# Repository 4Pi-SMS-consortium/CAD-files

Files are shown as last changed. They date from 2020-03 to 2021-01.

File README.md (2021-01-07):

# CAD-files

This is a repository of the CAD files for building a 4Pi-SMS
microscope.

* PartsList.xlsx Excel file with parts list including numbers and
  approximate cost.

* 4Pi-Oxford-packed is a snapshot of all the cad files, which includes
  fasteners from the content centre.

* STEP contains STEP files for machined parts.

* PDF contains drawings of parts and assemblies.

* File for 3d printed shutter mount 4pi-shutter-mount-V2.stl

* Pupil Plane Camera contains Solidworks files and drawings for mounting a board level camera in place of an objective at the pupil position.

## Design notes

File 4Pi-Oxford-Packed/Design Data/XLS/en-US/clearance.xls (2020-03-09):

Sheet: Ansi Unified Screw Threads
I | Sort Order -1
Fastener Type | Size | Shaft Diameters |  |  | Head Dimensions
 |  | Close | Normal | Loose | Diameter | Depth/Angle | Head Type
Flat Head Machine Screw (82) | #0 | 0.0635 | 0.07 | 0.073 | 0.119 | 82 | 2
Flat Head Machine Screw (82) | #1 | 0.076 | 0.081 | 0.089 | 0.146 | 82 | 2
Flat Head Machine Screw (82) | #2 | 0.089 | 0.096 | 0.1065 | 0.172 | 82 | 2
Flat Head Machine Screw (82) | #3 | 0.104 | 0.11 | 0.12 | 0.199 | 82 | 2
Flat Head Machine Screw (82) | #4 | 0.116 | 0.1285 | 0.136 | 0.225 | 82 | 2
Flat Head Machine Screw (82) | #5 | 0.1285 | 0.136 | 0.154 | 0.252 | 82 | 2
Flat Head Machine Screw (82) | #6 | 0.144 | 0.1495 | 0.1695 | 0.279 | 82 | 2
Flat Head Machine Screw (82) | #8 | 0.1695 | 0.177 | 0.1935 | 0.332 | 82 | 2
Flat Head Machine Screw (82) | #10 | 0.196 | 0.201 | 0.221 | 0.385 | 82 | 2
Flat Head Machine Screw (82) | #12 | 0.221 | 0.228 | 0.246 | 0.438 | 82 | 2
Flat Head Machine Screw (82) | 1/4 | 0.257 | 0.266 | 0.2812 | 0.507 | 82 | 2
Flat Head Machine Screw (82) | 5/16 | 0.323 | 0.332 | 0.3437 | 0.635 | 82 | 2
Flat Head Machine Screw (82) | 3/8 | 0.386 | 0.397 | 0.4062 | 0.762 | 82 | 2
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

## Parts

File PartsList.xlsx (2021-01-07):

Category | Part Number | Description | Vendor | Quantity | in Drawing
optomech | B90120B | Nexus breadboard, 900x1200 | Thorlabs | 1
optomech | PFA52507 | 800mm active isolation frame 900x1200 | Thorlabs | 1
optomech | PTA013 | air filter | Thorlabs | 1
optomech | PTA015 | compressor | Thorlabs | 1
optomech | PTA1006 | compressor oil | Thorlabs | 1
optomech | PBG52503/SPLS4 | Optical Breadboard 900 x 300 x 58mm M6/25mm/SPL 6mm top and bottom skin. Full Matrix both sides. | Thorlabs | 1
optomech - cavity | PRM05/M | High Precision Rotation Mount for Ø1/2" (12.5 mm) Optics, Metric | Thorlabs | 2
optomech | SS100-F3H | Suprema Mirror Mount, 1.0 in. Diameter, 3 Locking Hex-Broach, Front Load, 8-32 (M4) CLR | Newport | 12
optomech | ST1XY-A/M | XY Translator with 100 TPI Drives, Metric | Thorlabs | 2
optomech | U100-A-LH-3H | Precision Clear Edge Left Handed Mount, 1.0 in. Diameter, 3 Locking Allen-Keys | Newport | 1
optomech | U100-A3H | Precision Clear Edge Mount, 1.0 in. Diameter, 3 Locking Allen-Key Adjustment | Newport | 1
optomech | LMR1/M | Metric, Lens Mount for Ø1" Optics, Retaining Ring Included | Thorlabs | 6
optomech | 9481-M | Pint-Sized Prism Mount, 0.25 to 1.00 in., ±3.5 °, M4 | Newfocus | 1
optomech | NT64-566 | Optic Mount, 40.0mm Optic Diameter | Edmund Optics | 1
optomech | NT64-560 | Optic Mount, 25.0mm Optic Diameter | Edmund Optics | 1
optomech | LP-2A | XYZ θXθY Lens Positioner, 2.0 in. (50.8 mm) Diameter | Newport | 2 | Mounts for DM0 and DM1
optomech | KB25/M | Complete 25 mm x 25 mm Kinematic Base | Thorlabs | 1
optomech | RC1 | Rail Carrier, 1" x 1", 1/4" (M6) Counterbored Mounting Hole | Thorlabs | 1
optomech | RLA300/M | Dovetail Optical Rail, 300 mm, Metric | Thorlabs | 1
optomech | RLA600/M | Dovetail Optical Rail, 600 mm, Metric | Thorlabs | 1
shutter | NI USB-6002 | Multifunction I/O Device for shutter control | NI | 1
shutter | 04 RDI 132 | Cavity Bi-Stable Shutter | CVI Melles Griot | 2
optomech | M-GON40-U | Upper Goniometeric Stage, 40 x 40 x 20mm, ±5° Travel, Metric | Newport | 1
optomech | M-RS65 | Aperture Platform Rotation Stage, 65 mm, 10° Fine, Metric | Newport | 1
actuators | TRA12CC | Miniature Motorized Actuator, 12 mm Travel, DC Servo motor | Newport | 2
optomech | SP 60 (27.160.1212) | 12 mm Rectangular Aperture | Owis | 3 | AP1 and AP2
optomech | KSHM 90-LI-MDS (46.095.51KN) | 2 Inch Flip Mount | Owis | 2
custom | FAB-OX0001 | BS2/lens mount (replaces FAB-P0038) | Custom/Shop | 1
custom | FAB-OX0002 | Vertical mount for LMR/1 | Custom/Shop | 14
custom | FAB-OX0003 | Wedge base plate upper (repl. FAB-P0047) | Custom/Shop | 1
custom | FAB-OX0004 | Wedge base plate lower (repl. FAB-P0048) | Custom/Shop | 1
custom | FAB-OX0005 | Goniometer spacer (repl. FAB-CAM004) | Custom/Shop | 1
custom | FAB-OX0006 | Goniometer cube holder (repl. FAB-CAM003) | Custom/Shop | 1
custom | FAB-OX0007 | 40mm lens mount lower (FAB-P0044 variant) | Custom/Shop | 1
custom | FAB-OX0008 | Wedge support (mirror of FAB-P0051) | Custom/Shop | 1
custom | FAB-OX0009 | Overview mirror flip mount (repl. FAB-CAM002) | Custom/Shop | 1
custom | FAB-OX0010 | Alignment tool | Custom/Shop | 6
custom | FAB-OX0011 | Module 1 plate | Custom/Shop | 1
custom | FAB-OX0012 | Module 2 plate | Custom/Shop | 1
custom | FAB-OX0013 | Module 3 plate | Custom/Shop | 1
custom | FAB-OX0014 | Module 4 plate | Custom/Shop | 1
custom | FAB-OX0015 | 15mm lens holder with glue holes | Custom/Shop | 2
custom | FAB-OX0016 | Filter cube support - mirror of P0029 | Custom/Shop | 1
custom | FAB-OX0017 | Upper objective holder | Custom/Shop | 2
custom | FAB-OX0018 | Upper z-carriage bracket | Custom/Shop | 2
custom | FAB-OX0019 | Upper objective shim | Custom/Shop | 10
custom | FAB-OX0020 | Piezo pusher base component | Custom/Shop | 1
custom | FAB-OX0021 | Piezo pusher plate with cutout | Custom/Shop | 1
custom | FAB-OX0022 | Pizeo pusher actuator | Custom/Shop | 2
custom | FAB-OX0023 | Pizeo pusher plate | Custom/Shop | 3
custom | FAB-OX0024 | Pizeo pusher base with cutout | Custom/Shop | 1
custom | FAB-OX0025 | Upper objective pusher bar | Custom/Shop | 1
custom | FAB-OX0026 | Camera bracket crossbrace | Custom/Shop | 4
 | FAB-OX0027 | Upper Z carriage bracket block | Custom/Shop | 1
custom | FAB-P0001 | Tower Leg Foot | Custom/Shop | 2
custom | FAB-P0002 | Tower Leg | Custom/Shop | 2
custom | FAB-P0003 | ASI to Stage Bracket | Custom/Shop | 2
custom | FAB-P0004 | Lower Tower Plate | Custom/Shop | 1
custom | FAB-P0005 | Upper Tower Plate | Custom/Shop | 1
custom | FAB-P0008 | M-227 Clamp | Custom/Shop | 3
custom | FAB-P0009 | Sample Holder | Custom/Shop | 1
custom | FAB-P0010 | Lower Float Plate | Custom/Shop | 1
custom | FAB-P0015 | Lower OBJ Holder | Custom/Shop | 1
custom | FAB-P0018 | Mirror Mount, U100 | Custom/Shop | 2
custom | FAB-P0019 | Mirror Mount, SS100 | Custom/Shop | 6
custom | FAB-P0025 | Vertical Support Foot | Custom/Shop | 2
custom | FAB-P0026 | Vertical Support Leg | Custom/Shop | 1
custom | FAB-P0027 | Mirror Mount 45DEG SS100 | Custom/Shop | 2
custom | FAB-P0028 | Lens Mount, LMR1/M | Custom/Shop | 2
custom | FAB-P0029 | Filter Cube/Lens Support Upper | Custom/Shop | 1
custom | FAB-P0031 | Bridge Brace | Custom/Shop | 2
custom | FAB-P0032 | Filter Cube - Excitation | Custom/Shop | 2
custom | FAB-P0033 | Filter Cube - Emission | Custom/Shop | 2
custom | FAB-P0035 | Sample Holder for 2 Cover Glass | Custom/Shop | 10
custom | FAB-P0039 | Prism Glue-on Mount | Custom/Shop | 1
custom | FAB-P0044 | BS Lens Mount | Custom/Shop | 1
custom | FAB-P0048 | Wedge Only Mount UPPER | Custom/Shop | 1
custom | FAB-P0050 | Wedge Only Mount LOWER | Custom/Shop | 1
custom | FAB-P0051 | Wedge Support Large | Custom/Shop | 1
custom | FAB-P0052 | C-Mount Bolt for iXon | Custom/Shop | 1
custom | FAB-P0043 | Mount for widefield mirror | Custom/Shop | 1
custom | FAB-P0042 - w/sCMOS | Triangle iXon camera bracket | Custom/Shop | 2
custom | FAB-P0041 | sCMOS Mount Plate | Custom/Shop | 1
custom | FAB-CAM001 | Filter Wheel Mounting Bracket | Custom/Shop | 1
custom | FAB-CAM005 | Cavity Shutter Mount | Custom/Shop | 2
custom | FAB-CAM013 | Vertical Support with Cutout | Custom/Shop | 1
custom | ASF-10002 | Mirror Mount Jogged | Custom/Shop | 2
custom | ASF-10003 | Aperture Mount W/SLOT | Custom/Shop | 2
objectives | UPLSAPO 100XS | UPLSAPO 100XS; U PLAN S-APO 100X Silicone OIL OBJ,NA 1.35, WD 0.2 | Olympus | 2 | OBJ0 & OBJ1
adaptiveoptics | Multi-5.5 | Multi-DM MEMS Deformable Mirros | BMC | 2 | DM0 & DM1
optics - ImgSep | MRAK25-P01 | Right-Angle Prism Dielectric Mirror, 400 - 750 nm, L = 25.0 mm | Thorlabs | 1 | M17
optics | DBL14017/100 | 90.0MM EFL X 25.0MM Dia. ACHROMAT SINGLE-LAYER MgF2 VISIBLE | JML Optics | 2 | L3 and L4
optics | NT47-640 | Achromatic Lens 25mm Dia. x 85mm FL, VIS 0 Coating | Edmund Optics | 2 | L1 and L2
optics | NT49-280 | Achromatic Lens 40mm Dia. x 300mm FL, VIS 0 Coating | Edmund Optics | 3 | L0 and L5
optics | NT47-641 | Achromatic Lens 25mm Dia. x 100mm FL, VIS 0 Coating | Edmund Optics | 1
optics | W-4PISMSN | BK7 and quartz wedges | UVisIR | 1 | W0 and W1
optics | LAO-350.0-25.0 | Standard 400-700-nm Cemented Achromats, f 350 mm, diameter 25 mm | CVI Melles Griot | 2 | L6 and L7
optics | DLB-15-100PM | Achromatic doublets, 15 mm Dia. x 100 mm FL, 400-700 nm | OptoSigma | 2 | L8 and L9
optics | NT47-009 | Non-Polarizing Cube Beam splitter 25mm VIS | Edmund Optics | 1 | BS0
optics | 10FC16PB.3 | Broadband Polarizing Cube Beam splitter, 25.4 x 25.4 x 25.4 mm, 420-680 nm | Newport | 1
optics | NT49-002 | Polarizing Cube Beam splitter 25mm VIS | Edmund Optics | 1 | PBS0
optics | AQWP05M-600-UM-SP | Achromatic 1/4 wave plate 400800nm, unmounted (Custom) | Thorlabs | 2 | QWP1 and QWP1
optics | FSR-KG1 | Colored Glass Filter, 25.4 mm Diameter, Heat Absorbing, KG.1 | Newport | 1
optics | 10Z40ER.2 | Broadband Metallic Mirror, Zerodur, 25.4 mm Diameter, λ/20, 480-20,000 nm | Newport | 14 | M3-M16
optics-filters | FF01-446/523/600/677-25 | 446/523/600/677 nm BrightLine quad-band bandpass filter - 25 mm x 3.5 mm | Semrock | 2
optics-filters | ZT405/488/561/640rpcv2-UF1 | 405/488/561/640 Laser Dichroic Beam splitter, 17.5 x 24.0 mm | Chroma | 2 | DI0 and DI1
optics-filters | ET700/75m | Emissin filter in filter wheel Sputter/Hard Coated 700nm/75nm | Chroma | 1
optics-filters | ZET405/488/561/640mv2 | Quad-band bandpass filter in cavity | Chroma | 2
optics-filters | FF01-600/52-25 | 600/52 nm BrightLine® single-band bandpass filter | Semrock | 1
optics-filters | FF01-390/482/563/640-25 | 390/482/563/640 nm BrightLine® quad-band bandpass filter | Semrock | 1 | CF
Optomechanical | CXY1 | CXY1 - 30 mm Cage System, XY Translating Lens Mount for Ø1" Optics | Thorlabs | 2
Optomechanical | LM2XY_M | LM2XY/M - Translating Lens Mount for Ø2" Optics, 1 Retaining Ring Included, Metric | Thorlabs | 1
Optomechanical | RC1 | Dovetail Rail Carrier, 1/4" (M6) Counterbore | Thorlabs | 5
Optomechanical | RLA450_M | RLA450/M - Dovetail Optical Rail, 450 mm, Metric | Thorlabs | 1
Optomechanical | KM200 | Kinematic Mirror Mount for Ø2" Optics | Thorlabs | 1
Optomechanical | RC3 | Rail Carrier, Perpendicular Dovetail | Thorlabs | 2
Optomechanical | SM1SMA | SMA Fiber Adapter Plate with External SM1 (1.035"-40) Threads | Thorlabs | 1
Optomechanical | KCB1_M | KCB1/M - Right-Angle Kinematic Mirror Mount with Tapped Cage Rod Holes, 30 mm Cage System and SM1 Compatible, M4 and M6 Mounting Holes | Thorlabs | 1
Optomechanical | ER2 | Cage Assembly Rod, 2" Long, Ø6 mm | Thorlabs | 4
Optomechanical | ER4 | Cage Assembly Rod, 4" Long, Ø6 mm | Thorlabs | 4
Optomechanical | SM1Z | Z-Axis Translation Mount, 30 mm Cage Compatible | Thorlabs | 1
Optomechanical | CP08_M | SM1-Threaded 30 mm Cage Plate with Flexure Clamping, 1 Retaining Ring, M4 Tap | Thorlabs | 2
Optomechanical | LS-P642H0588A00_M | Ø1" (Ø25 mm) Posts for Polaris® Mirror Mounts | Thorlabs | 1
Optomechanical | PLS-P642H0300A00_M | Ø1" (Ø25 mm) Posts for Polaris® Mirror Mounts | Thorlabs | 1
Optomechanical | TR30-M | Ø12.7 mm Optical Post, SS, M4 Setscrew, M6 Tap, L = 30 mm | Thorlabs | 1
Optomechanical | PLS-P642H0457A00_M | Ø1" (Ø25 mm) Posts for Polaris® Mirror Mounts | Thorlabs | 1
Optomechanical | PLS-P642H0394A00_M | Ø1" (Ø25 mm) Posts for Polaris® Mirror Mounts | Thorlabs | 1
Optomechanical | CP02B | 30 mm Cage Mounting Bracket | Thorlabs | 1
Optomechanical | PH50_M | Ø12.7 mm Post Holder, Spring-Loaded Hex-Locking Thumbscrew, L=50 mm | Thorlabs | 1
Optomechanical | C4W | 30 mm Cage Cube | Thorlabs | 1
Optomechanical | SM1D12 | SM1 Lever-Actuated Iris Diaphragm (Ø0.8 - Ø12 mm) | Thorlabs | 10
Optomechanical | B4C/M | kinematic Cage Cube Platform for C4W/C6W, Metric | Thorlabs | 1
Optomechanical | FFM1 | 30-mm-Cage-Compatible Rectangular Filter Mount | Thorlabs | 1
Optics-diagnosis | DMSP805L | DMSP805L - Ø2" Shortpass Dichroic Mirror, 805 nm Cutoff | Thorlabs
Optomechanical | CXY2 | 60 mm Cage System Translating Lens Mount for Ø2" Optics | Thorlabs | 1
Optomechanical | Owis - 46.090.51KN | flip mirror holders with DC geared motor, with mechanical limit switches, for optics with ø 50 mm / 50.8 mm (2"), deflection to the right | Owis | 1
Optomechanical | KCB2_M | Right-Angle Kinematic Mirror Mount with Tapped Cage Rod Holes, 60 mm Cage System and SM2 Compatible, M4 and M6 Mounting Holes | Thorlabs | 1
Optomechanical | LC6W | 60 mm Cage Cube | Thorlabs | 1
Optomechanical | LB4C_M | Kinematic Prism Platform for 60 mm Cage Cube, Metric Taps | Thorlabs | 1
Optomechanical | LB5C1 | Ø2" Optic Mount for 60 mm Cage Cube with Setscrew Optic Retention | Thorlabs | 1
Optomechanical | 46.045.26KN | flip mirror holders with DC geared motor, with mechanical limit switches, for optics with ø 25 mm / 25.4 mm (1"), deflection to the left | Owis | 1
Optomechanical | RC12FC-P01 | Protected Silver Reflective Collimator, 450 nm - 20 µm, Ø12 mm Beam, FC/P | Thorlabs | 1
Optomechanical | K5X1 | 5-Axis Locking Kinematic Mount for Ø1" Optics | Thorlabs | 1
Optomechanical | RC2_M | Dovetail Rail Carrier, 50.8 mm x 25.4 mm, M6 Counterbore, M4 Taps | Thorlabs | 1
Optomechanical | PLS-P642H0293A00_M | Custom POLARIS Mounting Post, Height: 2.93 in | Thorlabs | 2
Optomechanical | PLS-P642H0335A00_M | Custom POLARIS Mounting Post, Height: 3.35 in | Thorlabs | 1
Optomechanical | PLS-P642H0537A00_M | Custom POLARIS Mounting Post, Height: 5.37 in | Thorlabs | 1
Optomechanical | PLS-P642H0446A00_M | Custom POLARIS Mounting Post, Height: 4.46 in | Thorlabs | 1
Optomechanical | PLS-P642H0495A00_M | Custom POLARIS Mounting Post, Height: 4.95 in | Thorlabs | 1
Optomechanical | LCPMA1 | Snap-On 60 mm Cage Mounting Bracket, #8 (M4) Slot | Thorlabs | 1
Optomechanical | TR100_M | Ø12.7 mm Optical Post, SS, M4 Setscrew, M6 Tap, L = 100 mm | Thorlabs | 1
Optomechanical | RA90_M | Right-Angle Clamp for Ø1/2" Posts, 5 mm Hex | Thorlabs | 1
Optomechanical | TR50_M | Ø12.7 mm Optical Post, SS, M4 Setscrew, M6 Tap, L = 50 mm £4.01 | Thorlabs | 1
Optomechanical | ER05 | Cage Assembly Rod, 1/2" Long, Ø6 mm | Thorlabs | 4
Optomechanical | LCP4S | 30 mm to 60 mm Cage Plate Adapter, 4 mm Thick | Thorlabs | 1
Optomechanical | SM1CPL10 | SM1 Lens Tube Flexure Sleeve Coupler, 1.0" Long | Thorlabs | 1
Optomechanical | SM1L05 | SM1 Lens Tube, 0.50" Thread Depth, One Retaining Ring Included | Thorlabs | 1
Optomechanical | DCC1545M | USB 2.0 CMOS Camera, 1280 x 1024, Monochrome Sensor | Thorlabs | 1
Optomechanical | CML15 | C-Mount Extension Tube, 15 mm Long | Thorlabs | 1
Optomechanical | 4-40 x 3/16 | Stainless Steel Screws | Thorlabs | 4
Optics | f = 500.0 mm, Ø1", N-BK7 Mounted Plano-Convex Round Cyl Lens, ARC: 650 - 1050 nm |  | Thorlabs | 1 | CY0
actuators | M-227.10 | High-Resolution DC-Mike Linear Actuator, 10 mm | PI | 3
actuators | C-863.11 | Mercury DC-Motor Controller, 1 Channel, with Wide-Range Power Supply | PI | 3
actuators | M-219.10 | M227 ball tip ends | PI | 3
actuators | LS-50 | ASI translation stage for tower | ASI | 2
actuators | LE-ZF | Micro-E linear encoder for LS-50 stages | ASI | 2
actuators | MS2 | MS2 LS 50 controller | ASI | 1
actuators | P-541.ZCD | Low-Profile Z-Nanopositioning Stage, 100μm, Cap. Sensors, Sub-D Connector | PI | 1
actuators | E-621.CR | Piezo Amplifier / Servo-Controller Module, 1 Channel, -30 to 130 V, Capacitive Sensor, USB, RS-232 | PI | 1
actuators | P-612.2SL | XY Nanopositioning System with 20 x 20 mm Aperture, 100 x 100 μm, Strain Gauge Sensors | PI | 1
actuators | E-621.SR | Piezo Amplifier / Servo-Controller Module, 1 Channel, -30 to 130 V, SGS-Sensor, USB, RS-232 | PI | 2
actuators | E-501.621 | 9.5-Chassis for up to four E-621 Modules, Power Supply | PI | 1
actuators | N-565.260 | high precision linear stage, replaces discontinued N664. 52mm travel | PI | 1
actuators | E-861.1A1 | NEXACT Controller, 1 Channel, Linear Encoder | PI | 1
actuators | U-751.24 | U-751 XY Stage with Piezomotors | PI | 1
actuators | C-867.2U2 | C-867.2U2 PILine® Motion Controller | PI | 1
actuators | MT1/M-Z8 | Motorized 12 mm Translation Stage, Metric | Thorlabs | 2
actuators | TDC001 | T-Cube DC Servo Motor Controller | Thorlabs | 2
actuators | TPS001 | 15 V Power Supply Unit for a Single T-Cube | Thorlabs | 2
lightsources | CPS532-C2 | Collimated Laser-Diode-Pumped DPSS Laser Module, 532 nm, 0.9 mW, Round Beam, Ø11 mm Housing | Thorlabs | 1 | LS0
lightsources | LP940-SF30 | LP940-SF30 - 940 nm, 30 mW, A Pin Code, SM Fiber-Pigtailed Laser Diode, FC/PC | Thorlabs | 1 | LS1
optomech | RC12FC-P01 | RC12FC-P01 - Protected Silver Reflective Collimator, 450 nm - 20 µm, Ø12 mm Beam, FC/PC | Thorlabs | 1
optomech | SM15RR | SM15 Retaining Ring for Ø15 mm Lens Mounts | Thorlabs | 2
detectors | ORCA FLASH C11440-22CU | SMS CAMERA | Hamamatsu | 1
detectors | CAMERALINK EXTENSION KIT | Frame Grabber CameraLink | Hamamatsu | 1
optomech | 84889 | USB Motorized Filter Wheel | Edmund Optics | 1
optomech | Stock #59-770 | 8-position Holder for 1" (25mm) Diameter Filters | Edmund Optics | 1
optomech | AJS100-0.5H-NL | High Precision Hex Adjustment Screw, 12.7 mm Travel, 100 TPI, Hex, No Lock | Newport | 2
hardware | NOA61 | MIL-A-3920 Optical Adhesive with Resiliency, 1 oz. | Thorlabs | 1
hardware | 91545A270 | Nylatron Flat Washer 3/8" Screw Size, .51" OD, .02"-.04" Thick, Pack of 5 | McMaster Carr | 1
hardware | 9657K258 | Steel Compression Spring Zinc-Pltd Music Wire,.250" L,.180" OD,.018" Wire, Pack of 12 | McMaster Carr | 1
hardware | 9001T15 | Music Wire Ultra-Precision Compression Spring .500" Length, .18" OD, .018" Wire Diameter, Pack of 3 | McMaster Carr | 1
hardware | 9434K25 | Music Wire Precision Compression Spring Zinc-Plated, .500" Length, .18" OD, .018" Wire, Pack of 5 | McMaster Carr | 1
hardware | 9657K46 | Steel Compression Spring Music Wire, 1.0" L,.187" OD, .014" Wire Diameter, Pack of 12 | McMaster Carr | 1
hardware | 1986K53 | Type 302 Stainless Steel Compression Spring 1.00" Length, .188" OD, .020" Wire Diameter, Pack of 6 | McMaster Carr | 1
hardware | 9434K32 | Music Wire Precision Compression Spring Zinc-Plated, .875" Length, .18" OD, .026" Wire, Pack of 5 | McMaster Carr | 1
Consumables | CSHP-No1.5-25 | High Precision Glass Cover Slip, box of 100, 25mm diameter, No. 1.5. | Bioscience Tools C B Consulting | 2
hardware | 1000T11 | Ultraviolet Light with Stand, 2 Tubes, 365 NM Wavelength | McMaster Carr | 1
hardware | 93285A210 | Metric Nylon Tip 18-8 SS Socket Set Screw M4 Size, 4mm Length, 0.7mm Pitch, Pack of 5 | McMaster Carr | 1
hardware | 16399-10 | Brass screws, M2 x 3, Pack of 10 | Ted Pella, Inc. | 1
hardware | 16399 | SEM Clips 1/2" Length, Pack of 10 | Ted Pella, Inc. | 1
hardware | 4629T67 | Compartmented Plastic Box Translucent, 4-24 Adj Compartments, 14" O'all Length | McMaster Carr | 4
tools | 8647A42 | Mitutoyo Standard Electronic Caliper 500-196-20, 0-6" (0-150mm) Range | McMaster Carr | 1
optics | PF20-03-P01 | Protected silver mirror, 2" | Thorlabs | 3 | FM0, M21 and M22
optics | PF10-03-P01 | Protected silver mirror, 1" | Thorlabs | 2
optomech | KM100 | 1" kinematic mirror mount | Thorlabs | 1
optomech | KM200 | 2" kinematic mirror mount | Thorlabs | 1
optics | AC508-300-A | 300mm achromat | Thorlabs | 1 | L12
optomech | LMR2_M | 2" fixed lens holder | Thorlabs | 1
hardware | MSVC4-20 | M4x20 high precision dowel pin, EN1.4125 steel | Misumi, Euro | 20
hardware | MSVC4-15 | M4x15 high precision dowel pin, EN 1.4125 steel | Misumi, Euro | 120
hardware | MSVC3-25 | M3x25 high precision dowel pin, EN 1.4125 steel | Misumi, Euro | 0
hardware | MSVC-15 | M3x15 high precision dowel pin, EN 1.4125 steel | Misumi, Euro | 20
hardware | MSVC3-10 | M3x10 high precision dowel pin, EN 1.4125 steel | Misumi, Euro | 0
hardware | MSVC3-8 | M3x8 high precision dowel pin, EN 1.4125 steel | Misumi, Euro | 0
hardware | TR-M4M6 | M6M-M4Fx10 thread adapter, pack of 10 | Newport | 12 pcs
hardware | SXSNS4-L0-P4-B8-H6.5-T1-E0.5 | M4 to 4h6 dowel adapter | Misumi, Euro | 20
Sample | CG15XH | Precision Cover Glasses, #1.5H Thickness, Ø25 mm, Pack of 1000 | Thorlabs | 100 x 10
hardware | 16399 | PELCO SEMClip™ Clips, pkg/10 | Ted Pella | 1
hardware | 16399-10 | PELCO SEMClip™ Screws, Brass, M2 x 3mm length, pkg/10 | Ted Pella | 1

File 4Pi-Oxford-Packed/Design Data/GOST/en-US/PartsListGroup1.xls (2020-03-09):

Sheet: Лист 1
Инв. № подл |  |  |  | Подп. и дата | Взам. инв. № | Инв. № дубл. |  |  | Подп. и дата
Формат | Зона | Поз. | Обозначение |  |  |  | Наименование |  |  |  |  |  | Кол. на исполнение
 |  |  |  |  |  |  |  |  |  |  |  | Лит.
 |  |  |  |  |  |  |  |  |  |  |  | Код
 |  |  |  |  |  |  |  | Изм. | Лист | № докум | Подпись |  | Дата
 |  |  |  |  |  |  |  | Разраб.
 |  |  |  |  |  |  |  | Пров.
 |  |  |  |  |  |  |  | Н.контр
 |  |  |  |  |  |  |  | Утв.
 |  |  |  |  |  |  |  |  |  |  |  |  |  | Копировал

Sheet: Лист 2
Инв. № подл |  |  |  | Подп. и дата | Взам. инв. № | Инв. № дубл. |  |  | Подп. и дата
Формат | Зона | Поз. | Обозначение |  |  |  | Наименование |  |  |  |  | Кол. на исполнение
 |  |  |  |  |  |  |  | Изм. | Лист | № докум. | Подп. | Дата
 |  |  |  |  |  |  |  |  |  |  |  |  | Копировал
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

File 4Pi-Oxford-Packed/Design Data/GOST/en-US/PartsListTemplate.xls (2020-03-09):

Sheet: Лист 1
 | Формат | Зона |  | Поз. |  | Обозначение |  |  |  | Наименование |  |  |  | Кол. | Приме-чание
Подп. и дата
Инв. № дубл.
Взам. инв. №
Подп. и дата
 | Изм. |  | Лист |  | № докум |  | Подпись | Дата
Инв. № подл | Разраб. |  |  |  |  |  |  |  |  |  | Литера |  | Лист |  |  | Листов
 | Пров.
 | Н.контр
 | Утв.
 |  |  |  |  |  |  |  |  | Копировал |  |  | Формат А4

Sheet: Лист 2
 | Формат | Зона |  | Поз. |  | Обозначение |  |  |  | Наименование |  | Кол. | Приме-чание
Подп. и дата
Инв. № дубл.
Взам. инв. №
Подп. и дата
Инв. № подл
 | Изм. |  | Лист |  | № докум. |  | Подп. |  | Дата
 |  |  |  |  |  |  |  | Копировал |  |  | Формат А4
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

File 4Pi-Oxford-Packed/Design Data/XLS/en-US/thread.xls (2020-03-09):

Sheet: Inch Tapping Threads
I Q X | Inch Tapping Threads |  | Sort Order - 5 |  | External |  |  |  |  |  |  | Internal
 |  |  |  |  |  | Major Dia |  | Pitch Dia |  | Minor Dia |  |  | Minor Dia |  | Pitch Dia |  | Major Dia |  | Tap Drill
Size | Size Suffix | Thread Designation | Custom Thread Designation | TPI | Class | Max | Min | Max | Min | Max | Min | Class | Min | Max | Min | Max | Min | Max | Basic
0.0600 |  | 0-48 | 0-48 | 48 | 2B | 0.0600 | 0.0540 | 0.0480 | 0.0435 | 0.0360 | 0.0330
0.0730 |  | 1-42 | 1-42 | 42 | 2B | 0.0750 | 0.0690 | 0.0620 | 0.0575 | 0.0490 | 0.0460
0.0860 |  | 2-32 | 2-32 | 32 | 2B | 0.0880 | 0.0820 | 0.0760 | 0.0710 | 0.0640 | 0.0600
0.0990 |  | 3-28 | 3-28 | 28 | 2B | 0.1010 | 0.0950 | 0.0880 | 0.0830 | 0.0750 | 0.0710
0.1120 |  | 4-24 | 4-24 | 24 | 2B | 0.1140 | 0.1080 | 0.1000 | 0.0950 | 0.0860 | 0.0820
0.1250 |  | 5-20 | 5-20 | 20 | 2B | 0.1300 | 0.1230 | 0.1120 | 0.1065 | 0.0940 | 0.0900
0.1380 |  | 6-20 | 6-20 | 20 | 2B | 0.1390 | 0.1320 | 0.1215 | 0.1155 | 0.1040 | 0.0990
0.1510 |  | 7-19 | 7-19 | 19 | 2B | 0.1540 | 0.1470 | 0.1345 | 0.1280 | 0.1150 | 0.1090
0.1640 |  | 8-18 | 8-18 | 18 | 2B | 0.1660 | 0.1590 | 0.1440 | 0.1375 | 0.1220 | 0.1160
0.1900 |  | 10-16 | 10-16 | 16 | 2B | 0.1890 | 0.1820 | 0.1650 | 0.1585 | 0.1410 | 0.1350
0.2160 |  | 12-14 | 12-14 | 14 | 2B | 0.2150 | 0.2080 | 0.1895 | 0.1825 | 0.1640 | 0.1570
0.2420 |  | 14-14 | 14-14 | 14 | 2B | 0.2410 | 0.2340 | 0.2130 | 0.2060 | 0.1850 | 0.1780
0.2500 |  | 1/4-14 | 1/4-14 | 14 | 2B | 0.2460 | 0.2370 | 0.2190 | 0.2110 | 0.1920 | 0.1850
0.3125 |  | 5/16-12 | 5/16-12 | 12 | 2B | 0.3150 | 0.3060 | 0.2795 | 0.2710 | 0.2440 | 0.2360
0.3750 |  | 3/8-12 | 3/8-12 | 12 | 2B | 0.3800 | 0.3710 | 0.3445 | 0.3350 | 0.3090 | 0.2990
0.4375 |  | 7/16-10 | 7/16-10 | 10 | 2B | 0.4400 | 0.4290 | 0.3995 | 0.3890 | 0.3590 | 0.3490
0.5000 |  | 1/2-10 | 1/2-10 | 10 | 2B | 0.5040 | 0.4930 | 0.4635 | 0.4530 | 0.4230 | 0.4130

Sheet: Metric Forming Screw Threads
M P X | Metric Forming Screw Threads |  | Sort Order - 6 |  | External |  |  |  |  |  |  | Internal
 |  |  |  |  |  | Major Dia |  | Pitch Dia |  | Minor Dia |  |  | Minor Dia |  | Pitch Dia |  | Major Dia |  | Tap Drill
Size | Size Suffix | Thread Designation | Custom Thread Designation | Pitch | Class | Max | Min | Max | Min | Max | Min | Class | Min | Max | Min | Max | Min | Max | Basic
1.5 |  | 1.5x0.5 | 1.5x0.5 | 0.5 | 6g | 1.520 | 1.380 | 1.215 | 1.110 | 0.910 | 0.840
1.5 |  | ST1.5x0.5 | ST1.5x0.5 | 0.5 | 6g | 1.520 | 1.380 | 1.215 | 1.110 | 0.910 | 0.840
1.9 |  | 1.9x0.6 | 1.9x0.6 | 0.6 | 6g | 1.900 | 1.760 | 1.570 | 1.465 | 1.240 | 1.170
1.9 |  | ST1.9x0.6 | ST1.9x0.6 | 0.6 | 6g | 1.900 | 1.760 | 1.570 | 1.465 | 1.240 | 1.170
2.2 |  | 2.2x0.8 | 2.2x0.8 | 0.8 | 6g | 2.240 | 2.100 | 1.935 | 1.810 | 1.630 | 1.520
2.2 |  | ST2.2x0.8 | ST2.2x0.8 | 0.8 | 6g | 2.240 | 2.100 | 1.935 | 1.810 | 1.630 | 1.520
2.6 |  | 2.6x0.9 | 2.6x0.9 | 0.9 | 6g | 2.570 | 2.430 | 2.235 | 2.115 | 1.900 | 1.800
2.6 |  | ST2.6x0.9 | ST2.6x0.9 | 0.9 | 6g | 2.570 | 2.430 | 2.235 | 2.115 | 1.900 | 1.800
2.9 |  | 2.9x1 | 2.9x1 | 1 | 6g | 2.900 | 2.760 | 2.540 | 2.420 | 2.180 | 2.080
2.9 |  | 2.9x1.1 | 2.9x1.1 | 1.1 | 6g | 2.900 | 2.760 | 2.540 | 2.420 | 2.180 | 2.080
2.9 |  | ST2.9x1.1 | ST2.9x1.1 | 1.1 | 6g | 2.900 | 2.760 | 2.540 | 2.420 | 2.180 | 2.080
2.9 |  | 2.9x1.3 | 2.9x1.3 | 1.3 | 6g | 2.900 | 2.720 | 2.540 | 2.355 | 1.890 | 1.700
2.9 |  | 2.9x1.4 | 2.9x1.4 | 1.4 | 6g | 2.900 | 2.720 | 2.340 | 2.175 | 1.780 | 1.630
3.3 |  | 3.3x1.3 | 3.3x1.3 | 1.3 | 6g | 3.300 | 3.120 | 2.795 | 2.665 | 2.290 | 2.210
3.3 |  | ST3.3x1.3 | ST3.3x1.3 | 1.3 | 6g | 3.300 | 3.120 | 2.795 | 2.665 | 2.290 | 2.210
3.5 |  | 3.5x1.3 | 3.5x1.3 | 1.3 | 6g | 3.530 | 3.350 | 3.085 | 2.930 | 2.640 | 2.510
3.5 |  | ST3.5x1.3 | ST3.5x1.3 | 1.3 | 6g | 3.530 | 3.350 | 3.085 | 2.930 | 2.640 | 2.510
3.5 |  | 3.5x1.6 | 3.5x1.6 | 1.6 | 6g | 3.530 | 3.350 | 2.920 | 2.755 | 2.310 | 2.160
3.5 |  | 3.5x3.2 | 3.5x3.2 | 3.2 | 6g | 3.530 | 3.310 | 2.800 | 2.600 | 2.070 | 1.890
3.9 |  | 3.9x1.3 | 3.9x1.3 | 1.3 | 6g | 3.910 | 3.730 | 3.415 | 3.250 | 2.920 | 2.770
3.9 |  | ST3.9x1.3 | ST3.9x1.3 | 1.3 | 6g | 3.910 | 3.730 | 3.415 | 3.250 | 2.920 | 2.770
3.9 |  | 3.9x1.6 | 3.9x1.6 | 1.6 | 6g | 3.910 | 3.730 | 3.300 | 3.135 | 2.690 | 2.540
3.9 |  | 3.9x3.2 | 3.9x3.2 | 3.2 | 6g | 3.910 | 3.690 | 3.180 | 2.980 | 2.450 | 2.270
4.2 |  | 4.2x1.4 | 4.2x1.4 | 1.4 | 6g | 4.220 | 4.040 | 3.660 | 3.495 | 3.100 | 2.950
4.2 |  | ST4.2x1.4 | ST4.2x1.4 | 1.4 | 6g | 4.220 | 4.040 | 3.660 | 3.495 | 3.100 | 2.950
4.2 |  | 4.2x1.6 | 4.2x1.6 | 1.6 | 6g | 4.220 | 4.040 | 3.610 | 3.445 | 3.000 | 2.850
4.2 |  | 4.2x3.2 | 4.2x3.2 | 3.2 | 6g | 4.220 | 4.000 | 3.380 | 3.180 | 2.540 | 2.360
4.8 |  | 4.8x1.6 | 4.8x1.6 | 1.6 | 6g | 4.800 | 4.620 | 4.190 | 4.025 | 3.580 | 3.430
4.8 |  | ST4.8x1.6 | ST4.8x1.6 | 1.6 | 6g | 4.800 | 4.620 | 4.190 | 4.025 | 3.580 | 3.430
4.8 |  | 4.8x1.8 | 4.8x1.8 | 1.8 | 6g | 4.800 | 4.620 | 4.065 | 3.885 | 3.330 | 3.150
4.8 |  | 4.8x3.2 | 4.8x3.2 | 3.2 | 6g | 4.800 | 4.580 | 3.960 | 3.760 | 3.120 | 2.940
5.5 |  | 5.5x1.8 | 5.5x1.8 | 1.8 | 6g | 5.460 | 5.280 | 4.815 | 4.635 | 4.170 | 3.990
5.5 |  | ST5.5x1.8 | ST5.5x1.8 | 1.8 | 6g | 5.460 | 5.280 | 4.815 | 4.635 | 4.170 | 3.990
6.3 |  | 6.3x1.8 | 6.3x1.8 | 1.8 | 6g | 6.250 | 6.030 | 5.565 | 5.365 | 4.880 | 4.700
6.3 |  | ST6.3x1.8 | ST6.3x1.8 | 1.8 | 6g | 6.250 | 6.030 | 5.565 | 5.365 | 4.880 | 4.700
8.0 |  | 8x2.1 | 8x2.1 | 2.1 | 6g | 8.000 | 7.780 | 7.100 | 6.885 | 6.200 | 5.990
8.0 |  | ST8x2.1 | ST8x2.1 | 2.1 | 6g | 8.000 | 7.780 | 7.100 | 6.885 | 6.200 | 5.990
9.5 |  | 9.5x2.1 | 9.5x2.1 | 2.1 | 6g | 9.650 | 9.430 | 8.750 | 8.510 | 7.850 | 7.590
9.5 |  | ST9.5x2.1 | ST9.5x2.1 | 2.1 | 6g | 9.650 | 9.430 | 8.750 | 8.510 | 7.850 | 7.590

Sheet: ISO Pipe Threads
M Q | ISO Pipe Threads |  | Sort Order - 9 |  | External |  |  |  |  |  |  | Internal
 |  |  |  |  |  | Major Dia |  | Pitch Dia |  | Minor Dia |  |  | Minor Dia |  | Pitch Dia |  | Major Dia |  | Tap Drill | Thread Depth | Thread Runouts
Size | Size Suffix | Thread Designation | Custom Thread Designation | TPI | Class | Max | Min | Max | Min | Max | Min | Class | Min | Max | Min | Max | Min | Max | Basic
7.723 |  | G7.723x0.907 | G 1/16 | 28 | A | 7.723 | 7.509 | 7.142 | 7.035 | 6.561 |  |  | 6.561 | 6.834 | 7.142 | 7.249 | 7.723 |  | 1.5875 | 15.446 | 4.5000
7.723 |  | G7.723x0.907 | G 1/16 | 28 | B | 7.723 | 7.509 | 7.142 | 6.928 | 6.561
9.728 |  | G9.728x0.907 | G 1/8 | 28 | A | 9.728 | 9.514 | 9.147 | 9.040 | 8.566 |  |  | 8.566 | 8.848 | 9.147 | 9.254 | 9.728 |  | 3.1750 | 19.456 | 4.5000
9.728 |  | G9.728x0.907 | G 1/8 | 28 | B | 9.728 | 9.514 | 9.147 | 8.933 | 8.566
13.157 |  | G13.157x1.337 | G 1/4 | 19 | A | 13.157 | 12.907 | 12.301 | 12.176 | 11.445 |  |  | 11.445 | 11.89 | 12.301 | 12.426 | 13.157 |  | 6.3500 | 26.314 | 6.5000
13.157 |  | G13.157x1.337 | G 1/4 | 19 | B | 13.157 | 12.907 | 12.301 | 12.051 | 11.445
16.662 |  | G16.662x1.337 | G 3/8 | 19 | A | 16.662 | 16.412 | 15.806 | 15.681 | 14.950 |  |  | 14.95 | 15.395 | 15.806 | 15.931 | 16.662 |  | 9.5250 | 33.324 | 6.5000
16.662 |  | G16.662x1.337 | G 3/8 | 19 | B | 16.662 | 16.412 | 15.806 | 15.556 | 14.950
20.955 |  | G20.955x1.814 | G 1/2 | 14 | A | 20.955 | 20.671 | 19.793 | 19.651 | 18.631 |  |  | 18.631 | 19.172 | 19.793 | 19.935 | 20.955 |  | 12.7000 | 41.910 | 8.5000
20.955 |  | G20.955x1.814 | G 1/2 | 14 | B | 20.955 | 20.671 | 19.793 | 19.509 | 18.631
22.911 |  | G22.911x1.814 | G 5/8 | 14 | A | 22.911 | 22.627 | 21.749 | 21.607 | 20.587 |  |  | 20.587 | 21.128 | 21.749 | 21.891 | 22.911 |  |  | 45.822 | 8.5000
22.911 |  | G22.911x1.814 | G 5/8 | 14 | B | 22.911 | 22.627 | 21.749 | 21.465 | 20.587
26.441 |  | G26.441x1.814 | G 3/4 | 14 | A | 26.441 | 26.157 | 25.279 | 25.137 | 24.117 |  |  | 24.117 | 24.658 | 25.279 | 25.421 | 26.441 |  | 15.8750 | 52.882 | 8.5000
26.441 |  | G26.441x1.814 | G 3/4 | 14 | B | 26.441 | 26.157 | 25.279 | 24.995 | 24.117
30.201 |  | G30.201x1.814 | G 7/8 | 14 | A | 30.201 | 29.917 | 29.039 | 28.897 | 27.877 |  |  | 27.877 | 28.418 | 29.039 | 29.181 | 30.201 |  | 22.2250 | 60.402 | 8.5000
30.201 |  | G30.201x1.814 | G 7/8 | 14 | B | 30.201 | 29.917 | 29.039 | 28.755 | 27.877
33.249 |  | G33.249x2.309 | G 1 | 11 | A | 33.249 | 32.889 | 31.770 | 31.590 | 30.291 |  |  | 30.291 | 30.931 | 31.77 | 31.95 | 33.249 |  | 25.4000 | 66.498 | 10.0000
33.249 |  | G33.249x2.309 | G 1 | 11 | B | 33.249 | 32.889 | 31.770 | 31.410 | 30.291
37.897 |  | G37.897x2.309 | G 1 1/8 | 11 | A | 37.897 | 37.537 | 36.418 | 36.238 | 34.939 |  |  | 34.939 | 35.579 | 36.418 | 36.598 | 37.897 |  | 28.5750 | 75.794 | 10.0000
37.897 |  | G37.897x2.309 | G 1 1/8 | 11 | B | 37.897 | 37.537 | 36.418 | 36.058 | 34.939
41.910 |  | G41.91x2.309 | G 1 1/4 | 11 | A | 41.910 | 41.550 | 40.431 | 40.251 | 38.952 |  |  | 38.952 | 39.592 | 40.431 | 40.611 | 41.910 |  | 31.7500 | 83.820 | 10.0000
41.910 |  | G41.91x2.309 | G 1 1/4 | 11 | B | 41.910 | 41.550 | 40.431 | 40.071 | 38.952
47.803 |  | G47.803x2.309 | G 1 1/2 | 11 | A | 47.803 | 47.443 | 46.324 | 46.144 | 44.845 |  |  | 44.845 | 45.485 | 46.324 | 46.504 | 47.803 |  | 38.1000 | 95.606 | 10.0000
47.803 |  | G47.803x2.309 | G 1 1/2 | 11 | B | 47.803 | 47.443 | 46.324 | 45.964 | 44.845
53.746 |  | G53.746x2.309 | G 1 3/4 | 11 | A | 53.746 | 53.386 | 52.267 | 52.087 | 50.788 |  |  | 50.788 | 51.428 | 52.267 | 52.447 | 53.746 |  | 44.4500 | 107.492 | 10.0000
53.746 |  | G53.746x2.309 | G 1 3/4 | 11 | B | 53.746 | 53.386 | 52.267 | 51.907 | 50.788
59.614 |  | G59.614x2.309 | G 2 | 11 | A | 59.614 | 59.254 | 58.135 | 57.955 | 56.656 |  |  | 56.656 | 57.296 | 58.135 | 58.315 | 59.614 |  | 50.8000 | 119.228 | 10.0000
59.614 |  | G59.614x2.309 | G 2 | 11 | B | 59.614 | 59.254 | 58.135 | 57.775 | 56.656
65.710 |  | G65.71x2.309 | G 2 1/4 | 11 | A | 65.710 | 65.276 | 64.231 | 64.014 | 62.752 |  |  | 62.752 | 63.392 | 64.231 | 64.448 | 65.710 |  | 57.1500 | 131.420 | 10.0000
65.710 |  | G65.71x2.309 | G 2 1/4 | 11 | B | 65.710 | 65.276 | 64.231 | 63.797 | 62.752
75.184 |  | G75.184x2.309 | G 2 1/2 | 11 | A | 75.184 | 74.750 | 73.705 | 73.488 | 72.226 |  |  | 72.226 | 72.866 | 73.705 | 73.922 | 75.184 |  |  | 150.368 | 10.0000
75.184 |  | G75.184x2.309 | G 2 1/2 | 11 | B | 75.184 | 74.750 | 73.705 | 73.271 | 72.226
81.534 |  | G81.534x2.309 | G 2 3/4 | 11 | A | 81.534 | 81.100 | 80.055 | 79.838 | 78.576 |  |  | 78.576 | 79.216 | 80.055 | 80.272 | 81.534 |  | 69.8500 | 163.068 | 10.0000
81.534 |  | G81.534x2.309 | G 2 3/4 | 11 | B | 81.534 | 81.100 | 80.055 | 79.621 | 78.576
87.884 |  | G87.884x2.309 | G 3 | 11 | A | 87.884 | 87.450 | 86.405 | 86.188 | 84.926 |  |  | 84.926 | 85.566 | 86.405 | 86.622 | 87.884 |  | 76.2000 | 175.768 | 10.0000
87.884 |  | G87.884x2.309 | G 3 | 11 | B | 87.884 | 87.450 | 86.405 | 85.971 | 84.926
100.330 |  | G100.33x2.309 | G 3 1/2 | 11 | A | 100.330 | 99.896 | 98.851 | 98.634 | 97.372 |  |  | 97.372 | 98.012 | 98.851 | 99.068 | 100.330 |  | 88.9000 | 200.660 | 10.0000
100.330 |  | G100.33x2.309 | G 3 1/2 | 11 | B | 100.330 | 99.896 | 98.851 | 98.417 | 97.372
113.030 |  | G113.03x2.309 | G 4 | 11 | A | 113.030 | 112.596 | 111.551 | 111.334 | 110.072 |  |  | 110.072 | 110.712 | 111.551 | 111.768 | 113.030 |  | 101.6000 | 226.060 | 10.0000
113.030 |  | G113.03x2.309 | G 4 | 11 | B | 113.030 | 112.596 | 111.551 | 111.117 | 110.072
125.730 |  | G125.73x2.309 | G 4 1/2 | 11 | A | 125.730 | 125.296 | 124.251 | 124.034 | 122.772 |  |  | 122.772 | 123.412 | 124.251 | 124.468 | 125.730 |  | 114.3000 | 251.460 | 10.0000
125.730 |  | G125.73x2.309 | G 4 1/2 | 11 | B | 125.730 | 125.296 | 124.251 | 123.817 | 122.772
138.430 |  | G138.43x2.309 | G 5 | 11 | A | 138.430 | 137.996 | 136.951 | 136.734 | 135.472 |  |  | 135.472 | 136.112 | 136.951 | 137.168 | 138.430 |  | 127.0000 | 276.860 | 10.0000
138.430 |  | G138.43x2.309 | G 5 | 11 | B | 138.430 | 137.996 | 136.951 | 136.517 | 135.472
151.130 |  | G151.13x2.309 | G 5 1/2 | 11 | A | 151.130 | 150.696 | 149.651 | 149.434 | 148.172 |  |  | 148.172 | 148.812 | 149.651 | 149.868 | 151.130 |  | 139.7000 | 302.260 | 10.0000
151.130 |  | G151.13x2.309 | G 5 1/2 | 11 | B | 151.130 | 150.696 | 149.651 | 149.217 | 148.172
163.830 |  | G163.83x2.309 | G 6 | 11 | A | 163.830 | 163.396 | 162.351 | 162.134 | 160.872 |  |  | 160.872 | 161.512 | 162.351 | 162.568 | 163.830 |  | 152.4000 | 327.660 | 10.0000
163.830 |  | G163.83x2.309 | G 6 | 11 | B | 163.830 | 163.396 | 162.351 | 161.917 | 160.872

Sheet: JIS Pipe Threads
M Q | JIS Pipe Threads |  | Sort Order -12 |  | External |  |  |  |  |  |  | Internal
 |  |  |  |  |  | Major Dia |  | Pitch Dia |  | Minor Dia |  |  | Minor Dia |  | Pitch Dia |  | Major Dia |  | Tap Drill | Thread Depth | Thread Runouts
Size | Size Suffix | Thread Designation | Custom Thread Designation | TPI | Class | Max | Min | Max | Min | Max | Min | Class | Min | Max | Min | Max | Min | Max | Basic |  | Basic
7.723 |  | G7.723x0.907 | G 1/16 | 28 | A | 7.723 | 7.509 | 7.142 | 7.035 | 6.561 |  |  | 6.561 | 6.834 | 7.142 | 7.249 | 7.723 |  | 1.5875 | 15.446 | 4.5000
7.723 |  | G7.723x0.907 | G 1/16 | 28 | B | 7.723 | 7.509 | 7.142 | 6.928 | 6.561
9.728 |  | G9.728x0.907 | G 1/8 | 28 | A | 9.728 | 9.514 | 9.147 | 9.040 | 8.566 |  |  | 8.566 | 8.848 | 9.147 | 9.254 | 9.728 |  | 3.1750 | 19.456 | 4.5000
9.728 |  | G9.728x0.907 | G 1/8 | 28 | B | 9.728 | 9.514 | 9.147 | 8.933 | 8.566
13.157 |  | G13.157x1.337 | G 1/4 | 19 | A | 13.157 | 12.907 | 12.301 | 12.176 | 11.445 |  |  | 11.445 | 11.89 | 12.301 | 12.426 | 13.157 |  | 6.3500 | 26.314 | 6.5000
13.157 |  | G13.157x1.337 | G 1/4 | 19 | B | 13.157 | 12.907 | 12.301 | 12.051 | 11.445
16.662 |  | G16.662x1.337 | G 3/8 | 19 | A | 16.662 | 16.412 | 15.806 | 15.681 | 14.950 |  |  | 14.95 | 15.395 | 15.806 | 15.931 | 16.662 |  | 9.5250 | 33.324 | 6.5000
16.662 |  | G16.662x1.337 | G 3/8 | 19 | B | 16.662 | 16.412 | 15.806 | 15.556 | 14.950
20.955 |  | G20.955x1.814 | G 1/2 | 14 | A | 20.955 | 20.671 | 19.793 | 19.651 | 18.631 |  |  | 18.631 | 19.172 | 19.793 | 19.935 | 20.955 |  | 12.7000 | 41.910 | 8.5000
20.955 |  | G20.955x1.814 | G 1/2 | 14 | B | 20.955 | 20.671 | 19.793 | 19.509 | 18.631
22.911 |  | G22.911x1.814 | G 5/8 | 14 | A | 22.911 | 22.627 | 21.749 | 21.607 | 20.587 |  |  | 20.587 | 21.128 | 21.749 | 21.891 | 22.911 |  |  | 45.822 | 8.5000
22.911 |  | G22.911x1.814 | G 5/8 | 14 | B | 22.911 | 22.627 | 21.749 | 21.465 | 20.587
26.441 |  | G26.441x1.814 | G 3/4 | 14 | A | 26.441 | 26.157 | 25.279 | 25.137 | 24.117 |  |  | 24.117 | 24.658 | 25.279 | 25.421 | 26.441 |  | 15.8750 | 52.882 | 8.5000
26.441 |  | G26.441x1.814 | G 3/4 | 14 | B | 26.441 | 26.157 | 25.279 | 24.995 | 24.117
30.201 |  | G30.201x1.814 | G 7/8 | 14 | A | 30.201 | 29.917 | 29.039 | 28.897 | 27.877 |  |  | 27.877 | 28.418 | 29.039 | 29.181 | 30.201 |  | 22.2250 | 60.402 | 8.8000
30.201 |  | G30.201x1.814 | G 7/8 | 14 | B | 30.201 | 29.917 | 29.039 | 28.755 | 27.877
33.249 |  | G33.249x2.309 | G 1 | 11 | A | 33.249 | 32.889 | 31.770 | 31.590 | 30.291 |  |  | 30.291 | 30.931 | 31.77 | 31.95 | 33.249 |  | 25.4000 | 66.498 | 10.0000
33.249 |  | G33.249x2.309 | G 1 | 11 | B | 33.249 | 32.889 | 31.770 | 31.410 | 30.291
37.897 |  | G37.897x2.309 | G 1 1/8 | 11 | A | 37.897 | 37.537 | 36.418 | 36.238 | 34.939 |  |  | 34.939 | 35.579 | 36.418 | 36.598 | 37.897 |  | 28.5750 | 75.794 | 10.0000
37.897 |  | G37.897x2.309 | G 1 1/8 | 11 | B | 37.897 | 37.537 | 36.418 | 36.058 | 34.939
41.910 |  | G41.91x2.309 | G 1 1/4 | 11 | A | 41.910 | 41.550 | 40.431 | 40.251 | 38.952 |  |  | 38.952 | 39.592 | 40.431 | 40.611 | 41.910 |  | 31.7500 | 83.820 | 10.0000
41.910 |  | G41.91x2.309 | G 1 1/4 | 11 | B | 41.910 | 41.550 | 40.431 | 40.071 | 38.952
47.803 |  | G47.803x2.309 | G 1 1/2 | 11 | A | 47.803 | 47.443 | 46.324 | 46.144 | 44.845 |  |  | 44.845 | 45.485 | 46.324 | 46.504 | 47.803 |  | 38.1000 | 95.606 | 10.0000
47.803 |  | G47.803x2.309 | G 1 1/2 | 11 | B | 47.803 | 47.443 | 46.324 | 45.964 | 44.845
53.746 |  | G53.746x2.309 | G 1 3/4 | 11 | A | 53.746 | 53.386 | 52.267 | 52.087 | 50.788 |  |  | 50.788 | 51.428 | 52.267 | 52.447 | 53.746 |  | 44.4500 | 107.492 | 10.0000
53.746 |  | G53.746x2.309 | G 1 3/4 | 11 | B | 53.746 | 53.386 | 52.267 | 51.907 | 50.788
59.614 |  | G59.614x2.309 | G 2 | 11 | A | 59.614 | 59.254 | 58.135 | 57.955 | 56.656 |  |  | 56.656 | 57.296 | 58.135 | 58.315 | 59.614 |  | 50.8000 | 119.228 | 10.0000
59.614 |  | G59.614x2.309 | G 2 | 11 | B | 59.614 | 59.254 | 58.135 | 57.775 | 56.656
65.710 |  | G65.71x2.309 | G 2 1/4 | 11 | A | 65.710 | 65.276 | 64.231 | 64.014 | 62.752 |  |  | 62.752 | 63.392 | 64.231 | 64.448 | 65.710 |  | 57.1500 | 131.420 | 10.0000
65.710 |  | G65.71x2.309 | G 2 1/4 | 11 | B | 65.710 | 65.276 | 64.231 | 63.797 | 62.752
75.184 |  | G75.184x2.309 | G 2 1/2 | 11 | A | 75.184 | 74.750 | 73.705 | 73.488 | 72.226 |  |  | 72.226 | 72.866 | 73.705 | 73.922 | 75.184 |  |  | 150.368 | 10.0000
75.184 |  | G75.184x2.309 | G 2 1/2 | 11 | B | 75.184 | 74.750 | 73.705 | 73.271 | 72.226
81.534 |  | G81.534x2.309 | G 2 3/4 | 11 | A | 81.534 | 81.100 | 80.055 | 79.838 | 78.576 |  |  | 78.576 | 79.216 | 80.055 | 80.272 | 81.534 |  | 69.8500 | 163.068 | 10.0000
81.534 |  | G81.534x2.309 | G 2 3/4 | 11 | B | 81.534 | 81.100 | 80.055 | 79.621 | 78.576
87.884 |  | G87.884x2.309 | G 3 | 11 | A | 87.884 | 87.450 | 86.405 | 86.188 | 84.926 |  |  | 84.926 | 85.566 | 86.405 | 86.622 | 87.884 |  | 76.2000 | 175.768 | 10.0000
87.884 |  | G87.884x2.309 | G 3 | 11 | B | 87.884 | 87.450 | 86.405 | 85.971 | 84.926
100.330 |  | G100.33x2.309 | G 3 1/2 | 11 | A | 100.330 | 99.896 | 98.851 | 98.634 | 97.372 |  |  | 97.372 | 98.012 | 98.851 | 99.068 | 100.330 |  | 88.9000 | 200.660 | 10.0000
100.330 |  | G100.33x2.309 | G 3 1/2 | 11 | B | 100.330 | 99.896 | 98.851 | 98.417 | 97.372
113.030 |  | G113.03x2.309 | G 4 | 11 | A | 113.030 | 112.596 | 111.551 | 111.334 | 110.072 |  |  | 110.072 | 110.712 | 111.551 | 111.768 | 113.030 |  | 101.6000 | 226.060 | 10.0000
113.030 |  | G113.03x2.309 | G 4 | 11 | B | 113.030 | 112.596 | 111.551 | 111.117 | 110.072
125.730 |  | G125.73x2.309 | G 4 1/2 | 11 | A | 125.730 | 125.296 | 124.251 | 124.034 | 122.772 |  |  | 122.772 | 123.412 | 124.251 | 124.468 | 125.730 |  | 114.3000 | 251.460 | 10.0000
125.730 |  | G125.73x2.309 | G 4 1/2 | 11 | B | 125.730 | 125.296 | 124.251 | 123.817 | 122.772
138.430 |  | G138.43x2.309 | G 5 | 11 | A | 138.430 | 137.996 | 136.951 | 136.734 | 135.472 |  |  | 135.472 | 136.112 | 136.951 | 137.168 | 138.430 |  | 127.0000 | 276.860 | 10.0000
138.430 |  | G138.43x2.309 | G 5 | 11 | B | 138.430 | 137.996 | 136.951 | 136.517 | 135.472
151.130 |  | G151.13x2.309 | G 5 1/2 | 11 | A | 151.130 | 150.696 | 149.651 | 149.434 | 148.172 |  |  | 148.172 | 148.812 | 149.651 | 149.868 | 151.130 |  | 139.7000 | 302.260 | 10.0000
151.130 |  | G151.13x2.309 | G 5 1/2 | 11 | B | 151.130 | 150.696 | 149.651 | 149.217 | 148.172
163.830 |  | G163.83x2.309 | G 6 | 11 | A | 163.830 | 163.396 | 162.351 | 162.134 | 160.872 |  |  | 160.872 | 161.512 | 162.351 | 162.568 | 163.830 |  | 152.4000 | 327.660 | 10.0000
163.830 |  | G163.83x2.309 | G 6 | 11 | B | 163.830 | 163.396 | 162.351 | 161.917 | 160.872

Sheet: DIN Pipe Threads
M Q | DIN Pipe Threads |  | Sort Order - 18 |  | External |  |  |  |  |  |  | Internal
 |  |  |  |  |  | Major Dia |  | Pitch Dia |  | Minor Dia |  |  | Minor Dia |  | Pitch Dia |  | Major Dia |  | Tap Drill | Thread Depth | Thread Runouts
Size | Size Suffix | Thread Designation | Custom Thread Designation | TPI | Class | Max | Min | Max | Min | Max | Min | Class | Min | Max | Min | Max | Min | Max | Basic
7.723 |  | G7.723x0.907 | G 1/16 | 28 | A | 7.723 | 7.509 | 7.142 | 7.035 | 6.561 |  |  | 6.561 | 6.834 | 7.142 | 7.249 | 7.723 |  | 1.5875 | 15.446 | 4.5000
7.723 |  | G7.723x0.907 | G 1/16 | 28 | B | 7.723 | 7.509 | 7.142 | 6.928 | 6.561
9.728 |  | G9.728x0.907 | G 1/8 | 28 | A | 9.728 | 9.514 | 9.147 | 9.040 | 8.566 |  |  | 8.566 | 8.848 | 9.147 | 9.254 | 9.728 |  | 3.1750 | 19.456 | 4.5000
9.728 |  | G9.728x0.907 | G 1/8 | 28 | B | 9.728 | 9.514 | 9.147 | 8.933 | 8.566
13.157 |  | G13.157x1.337 | G 1/4 | 19 | A | 13.157 | 12.907 | 12.301 | 12.176 | 11.445 |  |  | 11.445 | 11.89 | 12.301 | 12.426 | 13.157 |  | 6.3500 | 26.314 | 6.5000
13.157 |  | G13.157x1.337 | G 1/4 | 19 | B | 13.157 | 12.907 | 12.301 | 12.051 | 11.445
16.662 |  | G16.662x1.337 | G 3/8 | 19 | A | 16.662 | 16.412 | 15.806 | 15.681 | 14.950 |  |  | 14.95 | 15.395 | 15.806 | 15.931 | 16.662 |  | 9.5250 | 33.324 | 6.5000
16.662 |  | G16.662x1.337 | G 3/8 | 19 | B | 16.662 | 16.412 | 15.806 | 15.556 | 14.950
20.955 |  | G20.955x1.814 | G 1/2 | 14 | A | 20.955 | 20.671 | 19.793 | 19.651 | 18.631 |  |  | 18.631 | 19.172 | 19.793 | 19.935 | 20.955 |  | 12.7000 | 41.910 | 8.5000
20.955 |  | G20.955x1.814 | G 1/2 | 14 | B | 20.955 | 20.671 | 19.793 | 19.509 | 18.631
22.911 |  | G22.911x1.814 | G 5/8 | 14 | A | 22.911 | 22.627 | 21.749 | 21.607 | 20.587 |  |  | 20.587 | 21.128 | 21.749 | 21.891 | 22.911 |  |  | 45.822 | 8.5000
22.911 |  | G22.911x1.814 | G 5/8 | 14 | B | 22.911 | 22.627 | 21.749 | 21.465 | 20.587
26.441 |  | G26.441x1.814 | G 3/4 | 14 | A | 26.441 | 26.157 | 25.279 | 25.137 | 24.117 |  |  | 24.117 | 24.658 | 25.279 | 25.421 | 26.441 |  | 15.8750 | 52.882 | 8.5000
26.441 |  | G26.441x1.814 | G 3/4 | 14 | B | 26.441 | 26.157 | 25.279 | 24.995 | 24.117
30.201 |  | G30.201x1.814 | G 7/8 | 14 | A | 30.201 | 29.917 | 29.039 | 28.897 | 27.877 |  |  | 27.877 | 28.418 | 29.039 | 29.181 | 30.201 |  | 22.2250 | 60.402 | 8.5000
30.201 |  | G30.201x1.814 | G 7/8 | 14 | B | 30.201 | 29.917 | 29.039 | 28.755 | 27.877
33.249 |  | G33.249x2.309 | G 1 | 11 | A | 33.249 | 32.889 | 31.770 | 31.590 | 30.291 |  |  | 30.291 | 30.931 | 31.77 | 31.95 | 33.249 |  | 25.4000 | 66.498 | 10.5000
33.249 |  | G33.249x2.309 | G 1 | 11 | B | 33.249 | 32.889 | 31.770 | 31.410 | 30.291
37.897 |  | G37.897x2.309 | G 1 1/8 | 11 | A | 37.897 | 37.537 | 36.418 | 36.238 | 34.939 |  |  | 34.939 | 35.579 | 36.418 | 36.598 | 37.897 |  | 28.5750 | 75.794 | 10.5000
37.897 |  | G37.897x2.309 | G 1 1/8 | 11 | B | 37.897 | 37.537 | 36.418 | 36.058 | 34.939
41.910 |  | G41.91x2.309 | G 1 1/4 | 11 | A | 41.910 | 41.550 | 40.431 | 40.251 | 38.952 |  |  | 38.952 | 39.592 | 40.431 | 40.611 | 41.910 |  | 31.7500 | 83.820 | 10.5000
41.910 |  | G41.91x2.309 | G 1 1/4 | 11 | B | 41.910 | 41.550 | 40.431 | 40.071 | 38.952
47.803 |  | G47.803x2.309 | G 1 1/2 | 11 | A | 47.803 | 47.443 | 46.324 | 46.144 | 44.845 |  |  | 44.845 | 45.485 | 46.324 | 46.504 | 47.803 |  | 38.1000 | 95.606 | 10.5000
47.803 |  | G47.803x2.309 | G 1 1/2 | 11 | B | 47.803 | 47.443 | 46.324 | 45.964 | 44.845
53.746 |  | G53.746x2.309 | G 1 3/4 | 11 | A | 53.746 | 53.386 | 52.267 | 52.087 | 50.788 |  |  | 50.788 | 51.428 | 52.267 | 52.447 | 53.746 |  | 44.4500 | 107.492 | 10.5000
53.746 |  | G53.746x2.309 | G 1 3/4 | 11 | B | 53.746 | 53.386 | 52.267 | 51.907 | 50.788
59.614 |  | G59.614x2.309 | G 2 | 11 | A | 59.614 | 59.254 | 58.135 | 57.955 | 56.656 |  |  | 56.656 | 57.296 | 58.135 | 58.315 | 59.614 |  | 50.8000 | 119.228 | 10.5000
59.614 |  | G59.614x2.309 | G 2 | 11 | B | 59.614 | 59.254 | 58.135 | 57.775 | 56.656
65.710 |  | G65.71x2.309 | G 2 1/4 | 11 | A | 65.710 | 65.276 | 64.231 | 64.014 | 62.752 |  |  | 62.752 | 63.392 | 64.231 | 64.448 | 65.710 |  | 57.1500 | 131.420 | 10.5000
65.710 |  | G65.71x2.309 | G 2 1/4 | 11 | B | 65.710 | 65.276 | 64.231 | 63.797 | 62.752
75.184 |  | G75.184x2.309 | G 2 1/2 | 11 | A | 75.184 | 74.750 | 73.705 | 73.488 | 72.226 |  |  | 72.226 | 72.866 | 73.705 | 73.922 | 75.184 |  |  | 150.368 | 10.5000
75.184 |  | G75.184x2.309 | G 2 1/2 | 11 | B | 75.184 | 74.750 | 73.705 | 73.271 | 72.226
81.534 |  | G81.534x2.309 | G 2 3/4 | 11 | A | 81.534 | 81.100 | 80.055 | 79.838 | 78.576 |  |  | 78.576 | 79.216 | 80.055 | 80.272 | 81.534 |  | 69.8500 | 163.068 | 10.5000
81.534 |  | G81.534x2.309 | G 2 3/4 | 11 | B | 81.534 | 81.100 | 80.055 | 79.621 | 78.576
87.884 |  | G87.884x2.309 | G 3 | 11 | A | 87.884 | 87.450 | 86.405 | 86.188 | 84.926 |  |  | 84.926 | 85.566 | 86.405 | 86.622 | 87.884 |  | 76.2000 | 175.768 | 10.5000
87.884 |  | G87.884x2.309 | G 3 | 11 | B | 87.884 | 87.450 | 86.405 | 85.971 | 84.926
100.330 |  | G100.33x2.309 | G 3 1/2 | 11 | A | 100.330 | 99.896 | 98.851 | 98.634 | 97.372 |  |  | 97.372 | 98.012 | 98.851 | 99.068 | 100.330 |  | 88.9000 | 200.660 | 10.5000
100.330 |  | G100.33x2.309 | G 3 1/2 | 11 | B | 100.330 | 99.896 | 98.851 | 98.417 | 97.372
113.030 |  | G113.03x2.309 | G 4 | 11 | A | 113.030 | 112.596 | 111.551 | 111.334 | 110.072 |  |  | 110.072 | 110.712 | 111.551 | 111.768 | 113.030 |  | 101.6000 | 226.060 | 10.5000
113.030 |  | G113.03x2.309 | G 4 | 11 | B | 113.030 | 112.596 | 111.551 | 111.117 | 110.072
125.730 |  | G125.73x2.309 | G 4 1/2 | 11 | A | 125.730 | 125.296 | 124.251 | 124.034 | 122.772 |  |  | 122.772 | 123.412 | 124.251 | 124.468 | 125.730 |  | 114.3000 | 251.460 | 10.5000
125.730 |  | G125.73x2.309 | G 4 1/2 | 11 | B | 125.730 | 125.296 | 124.251 | 123.817 | 122.772
138.430 |  | G138.43x2.309 | G 5 | 11 | A | 138.430 | 137.996 | 136.951 | 136.734 | 135.472 |  |  | 135.472 | 136.112 | 136.951 | 137.168 | 138.430 |  | 127.0000 | 276.860 | 10.5000
138.430 |  | G138.43x2.309 | G 5 | 11 | B | 138.430 | 137.996 | 136.951 | 136.517 | 135.472
151.130 |  | G151.13x2.309 | G 5 1/2 | 11 | A | 151.130 | 150.696 | 149.651 | 149.434 | 148.172 |  |  | 148.172 | 148.812 | 149.651 | 149.868 | 151.130 |  | 139.7000 | 302.260 | 10.5000
151.130 |  | G151.13x2.309 | G 5 1/2 | 11 | B | 151.130 | 150.696 | 149.651 | 149.217 | 148.172
163.830 |  | G163.83x2.309 | G 6 | 11 | A | 163.830 | 163.396 | 162.351 | 162.134 | 160.872 |  |  | 160.872 | 161.512 | 162.351 | 162.568 | 163.830 |  | 152.4000 | 327.660 | 10.5000
163.830 |  | G163.83x2.309 | G 6 | 11 | B | 163.830 | 163.396 | 162.351 | 161.917 | 160.872
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

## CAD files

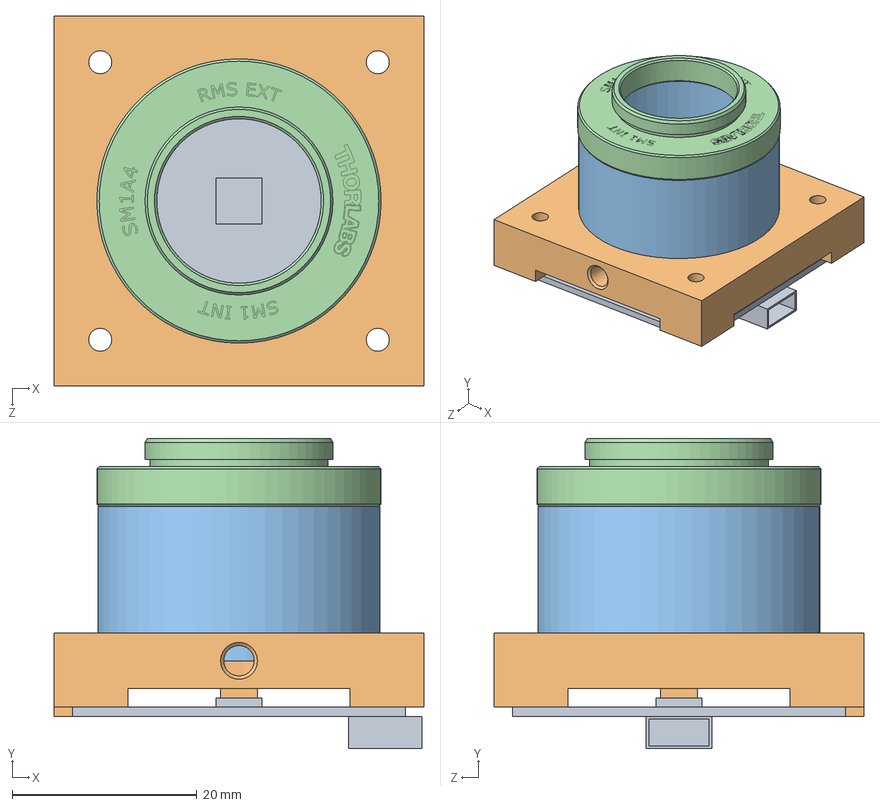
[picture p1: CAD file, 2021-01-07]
Pupil Plane Camera/Pupil Plane Camera.SLDASM
40.0 x 33.5 x 40.0 mm
84-933 - Board Level Camera
FAB-CH001 - Camera Holder
FAB-CH003 - 25 mm SM1 Mount
SM1A4 - Ext RMS to Int SM1

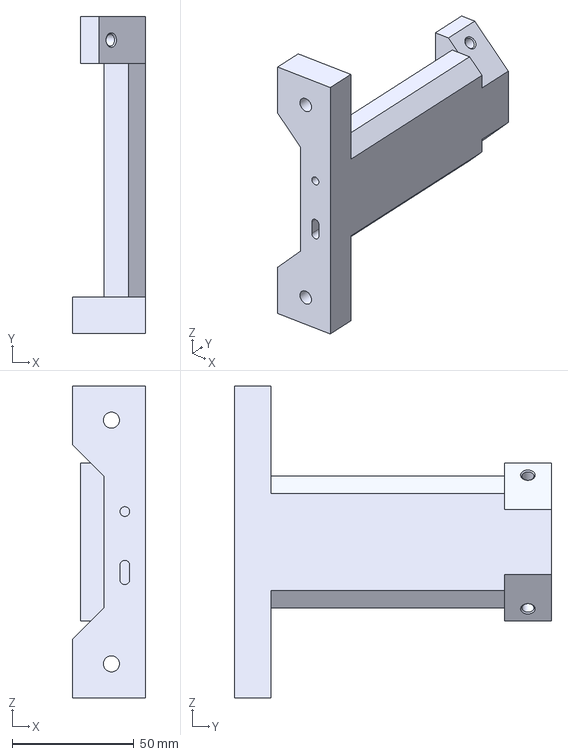
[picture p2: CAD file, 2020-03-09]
STEP/FAB-CAM006 - Main Rail Carrier - V2.stp
30.0 x 130.1 x 128.0 mm

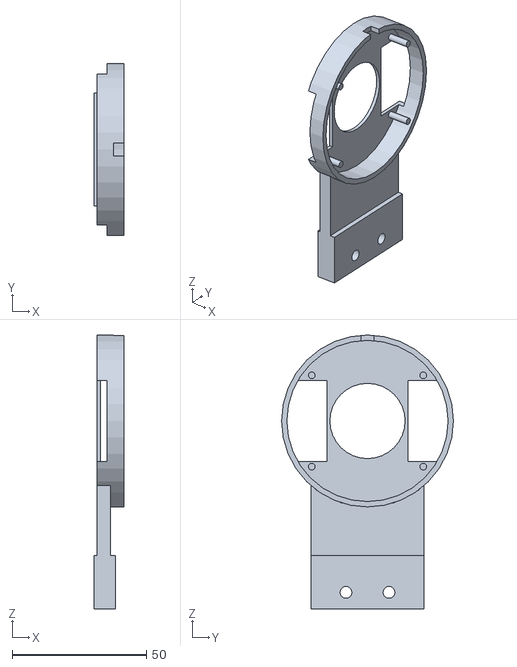
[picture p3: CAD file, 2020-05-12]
4pi-shutter-mount-V2.stl
11.0 x 64.0 x 102.0

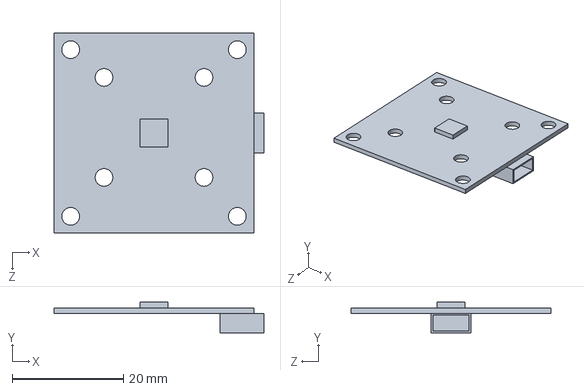
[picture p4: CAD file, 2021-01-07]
Pupil Plane Camera/Commercial Parts/Edumond Optics/Cameras/84-933 - Board Level Camera.SLDPRT
37.8 x 5.50 x 36.0 mm

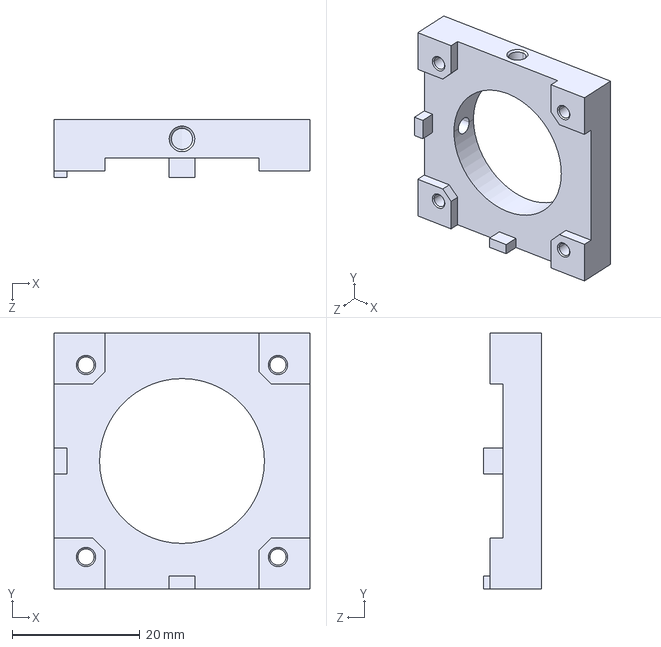
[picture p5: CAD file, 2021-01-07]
Pupil Plane Camera/FAB-CH001 - Camera Holder/FAB-CH001 - Camera Holder.STEP
40.0 x 40.0 x 9.00 mm

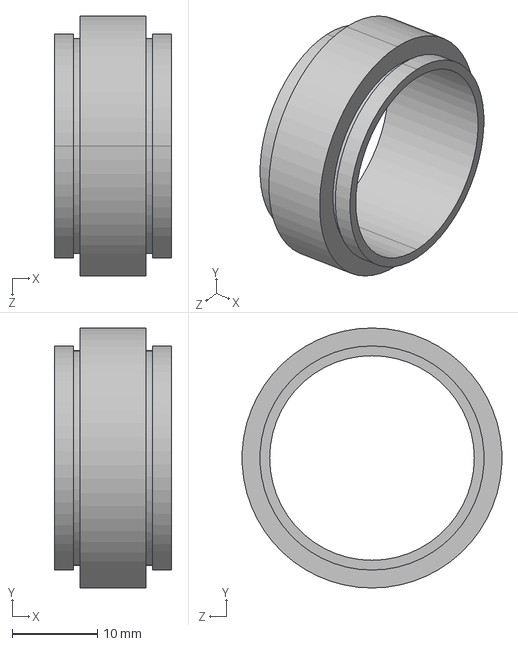
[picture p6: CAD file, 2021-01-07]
Pupil Plane Camera/FAB-CH002 - 19 mm SM1 Mount/FAB-CH002 - 19 mm SM1 Mount.STEP
13.8 x 30.5 x 30.5 mm

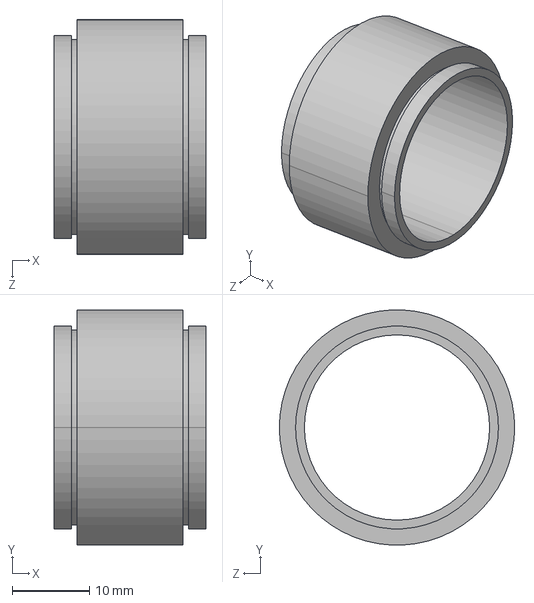
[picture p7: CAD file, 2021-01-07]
Pupil Plane Camera/FAB-CH003 - 25 mm SM1 Mount/FAB-CH003 - 25 mm SM1 Mount.STEP
19.7 x 30.5 x 30.5 mm

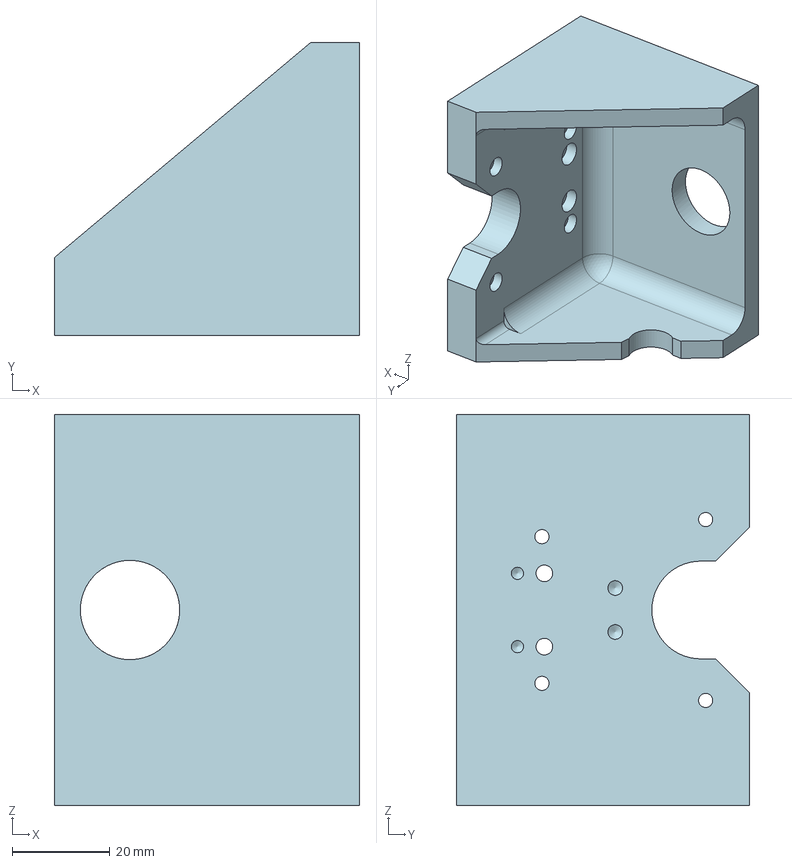
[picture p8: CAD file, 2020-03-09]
STEP/FAB-OX0017.stp
62.5 x 60.0 x 80.0 mm

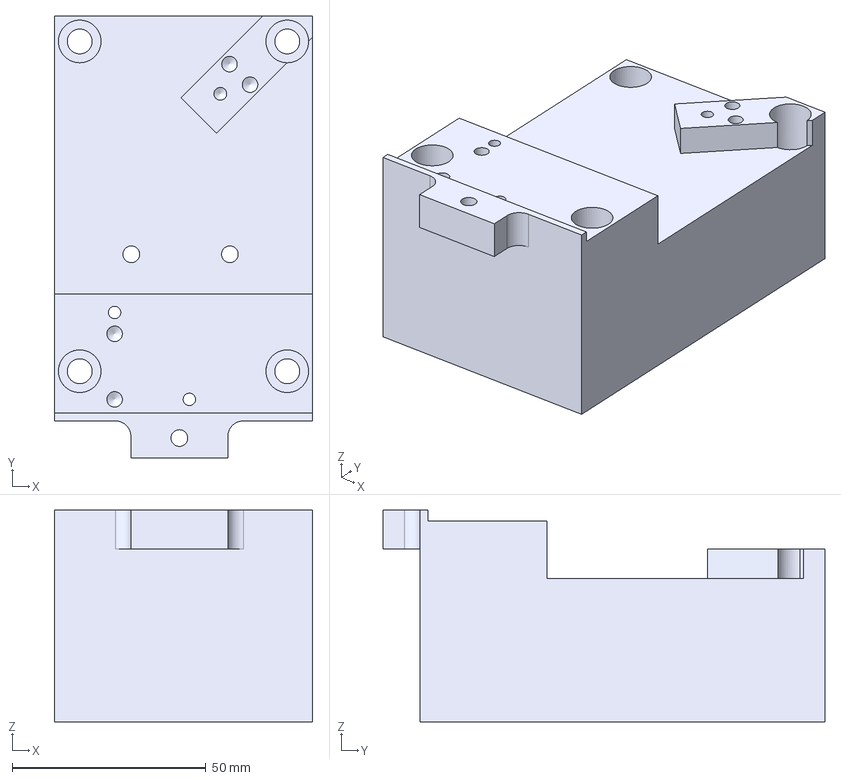
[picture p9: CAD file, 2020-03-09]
STEP/FAB-P0030 Filter Cube Support- Lower.stp
66.5 x 113.8 x 54.6 mm

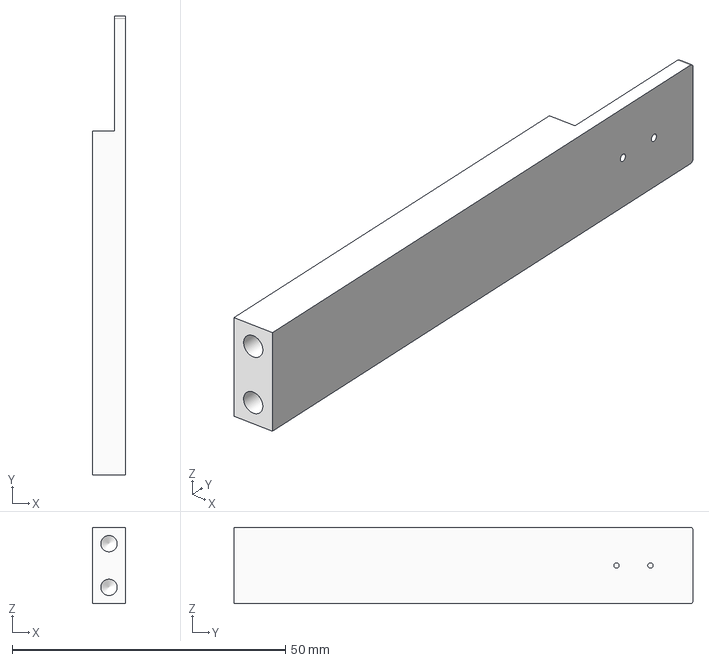
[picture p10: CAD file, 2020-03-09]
STEP/FAB-OX0010-AlignmentTool.70mm.stp
6.00 x 84.0 x 14.0 mm

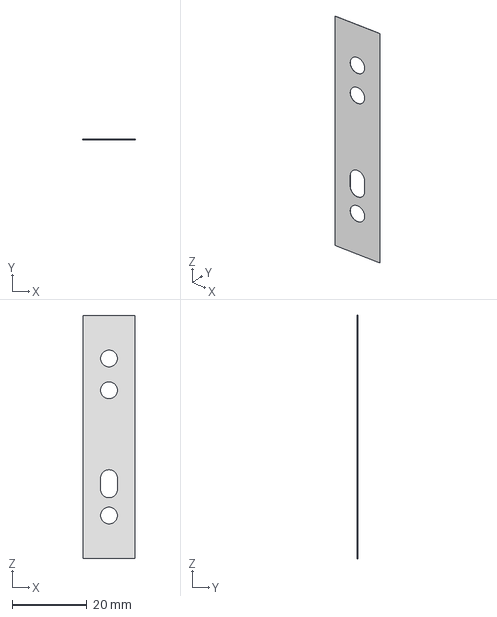
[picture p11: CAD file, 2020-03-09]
STEP/FAB-OX0019-UpperObjectiveShim.stp
14.0 x 0.05 x 65.0 mm

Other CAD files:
4Pi-Oxford-Packed/Templates/English/ANSI (in).dwg
4Pi-Oxford-Packed/Templates/Metric/BSI.dwg
4Pi-Oxford-Packed/Templates/standard.dwg
4Pi-Oxford-Packed/Templates/Metric/DIN.dwg
4Pi-Oxford-Packed/Templates/Metric/ANSI (mm).dwg
4Pi-Oxford-Packed/Templates/Metric/GB.dwg
4Pi-Oxford-Packed/Templates/Metric/ISO.dwg
4Pi-Oxford-Packed/Design Data/AIT/Mold Design/mold design stop pin.ipt
4Pi-Oxford-Packed/Design Data/Cable & Harness/en-US/harness.iam
4Pi-Oxford-Packed/Design Data/Tube & Pipe/en-US/piping runs.iam
4Pi-Oxford-Packed/Templates/English/Mold Design (in).iam
4Pi-Oxford-Packed/Templates/English/Sheet Metal (in).ipt
4Pi-Oxford-Packed/Templates/English/Standard (in).iam
4Pi-Oxford-Packed/Templates/English/Standard (in).ipt
4Pi-Oxford-Packed/Templates/English/Weldment (ANSI).iam
4Pi-Oxford-Packed/Templates/Metric/GOST.dwg
4Pi-Oxford-Packed/Templates/Metric/JIS.dwg
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

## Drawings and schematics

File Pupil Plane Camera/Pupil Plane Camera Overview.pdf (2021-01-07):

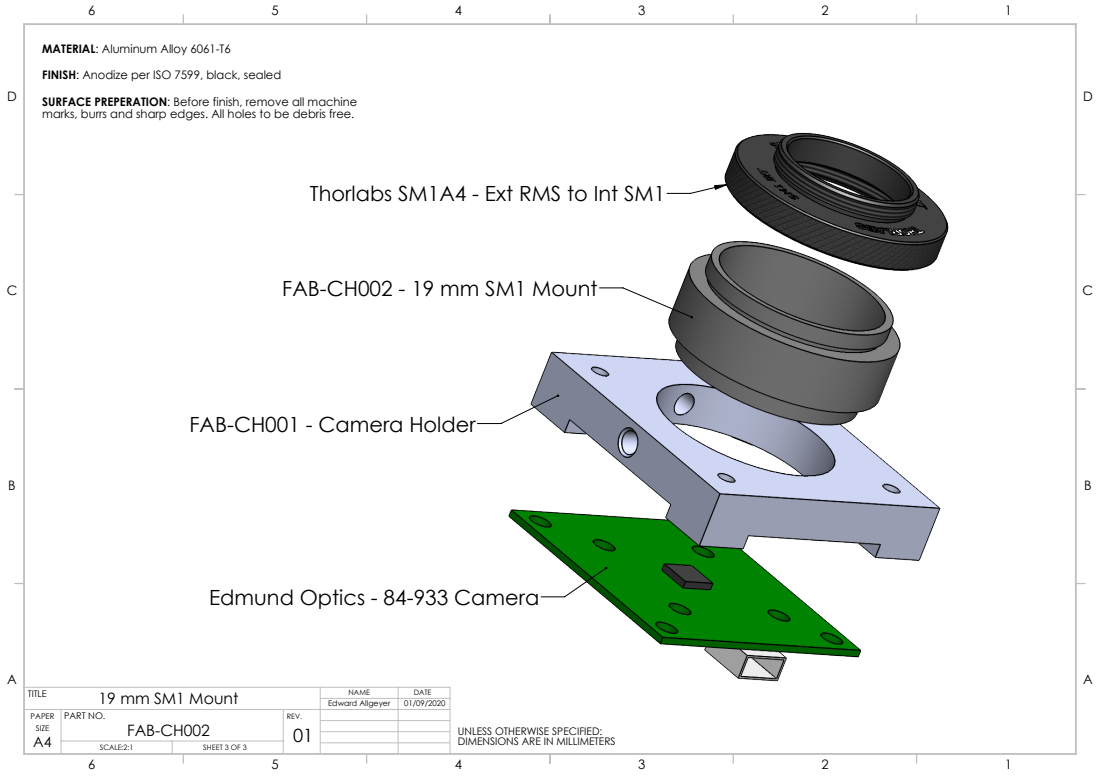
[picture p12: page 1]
SCALE:2:1; SHEET 3 OF 3; SIZE; UNLESS OTHERWISE SPECIFIED:

MATERIAL: Aluminum Alloy 6061-T6
FINISH: Anodize per ISO 7599, black, sealed
SURFACE PREPERATION: Before finish, remove all machine
marks, burrs and sharp edges. All holes to be debris free.

Thorlabs SM1A4 - Ext RMS to Int SM1

FAB-CH002 - 19 mm SM1 Mount

FAB-CH001 - Camera Holder

Edmund Optics - 84-933 Camera

TITLE 19 mm SM1 Mount | NAME | DATE

Edward Allgeyer | 01/09/2020

PAPER | PART NO. FAB-CH002 | REV. 01

DIMENSIONS ARE IN MILLIMETERS

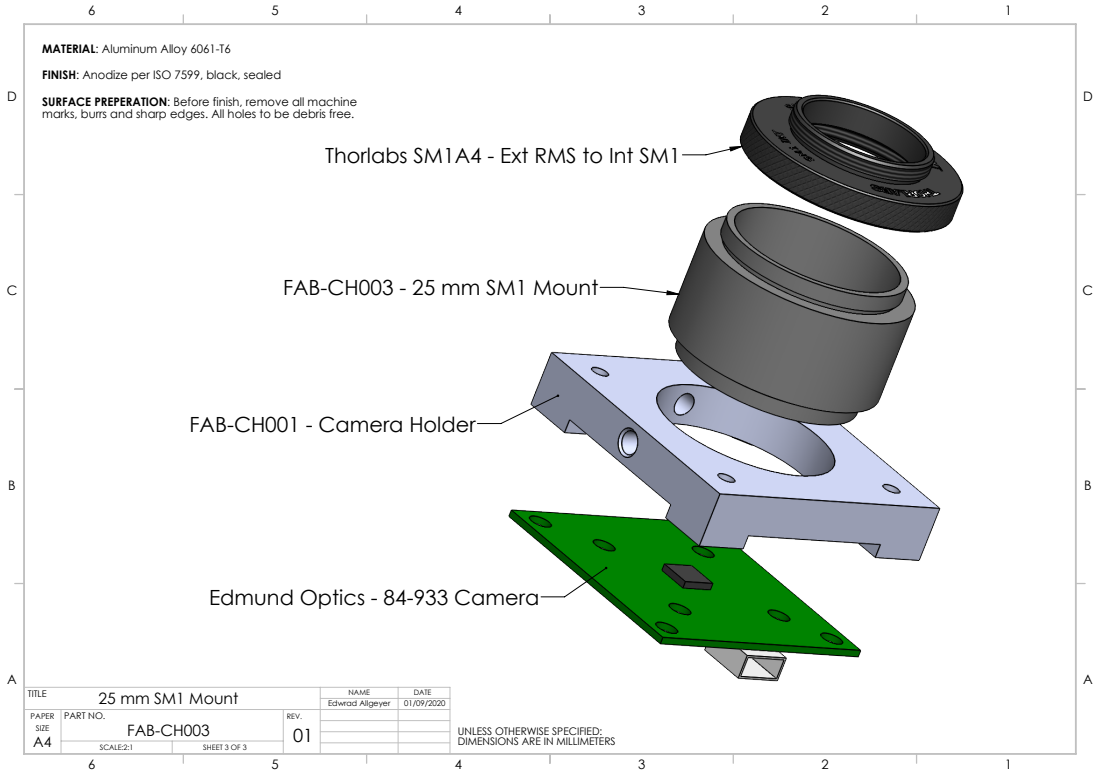
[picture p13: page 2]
SCALE:2:1; SHEET 3 OF 3; SIZE; UNLESS OTHERWISE SPECIFIED:

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

Thorlabs SM1A4 - Ext RMS to Int SM1

FAB-CH003 - 25 mm SM1 Mount

FAB-CH001 - Camera Holder

Edmund Optics - 84-933 Camera

TITLE 25 mm SM1 Mount | NAME | DATE

Edwrad Allgeyer | 01/09/2020

PAPER | PART NO. FAB-CH003 | REV. 01

DIMENSIONS ARE IN MILLIMETERS

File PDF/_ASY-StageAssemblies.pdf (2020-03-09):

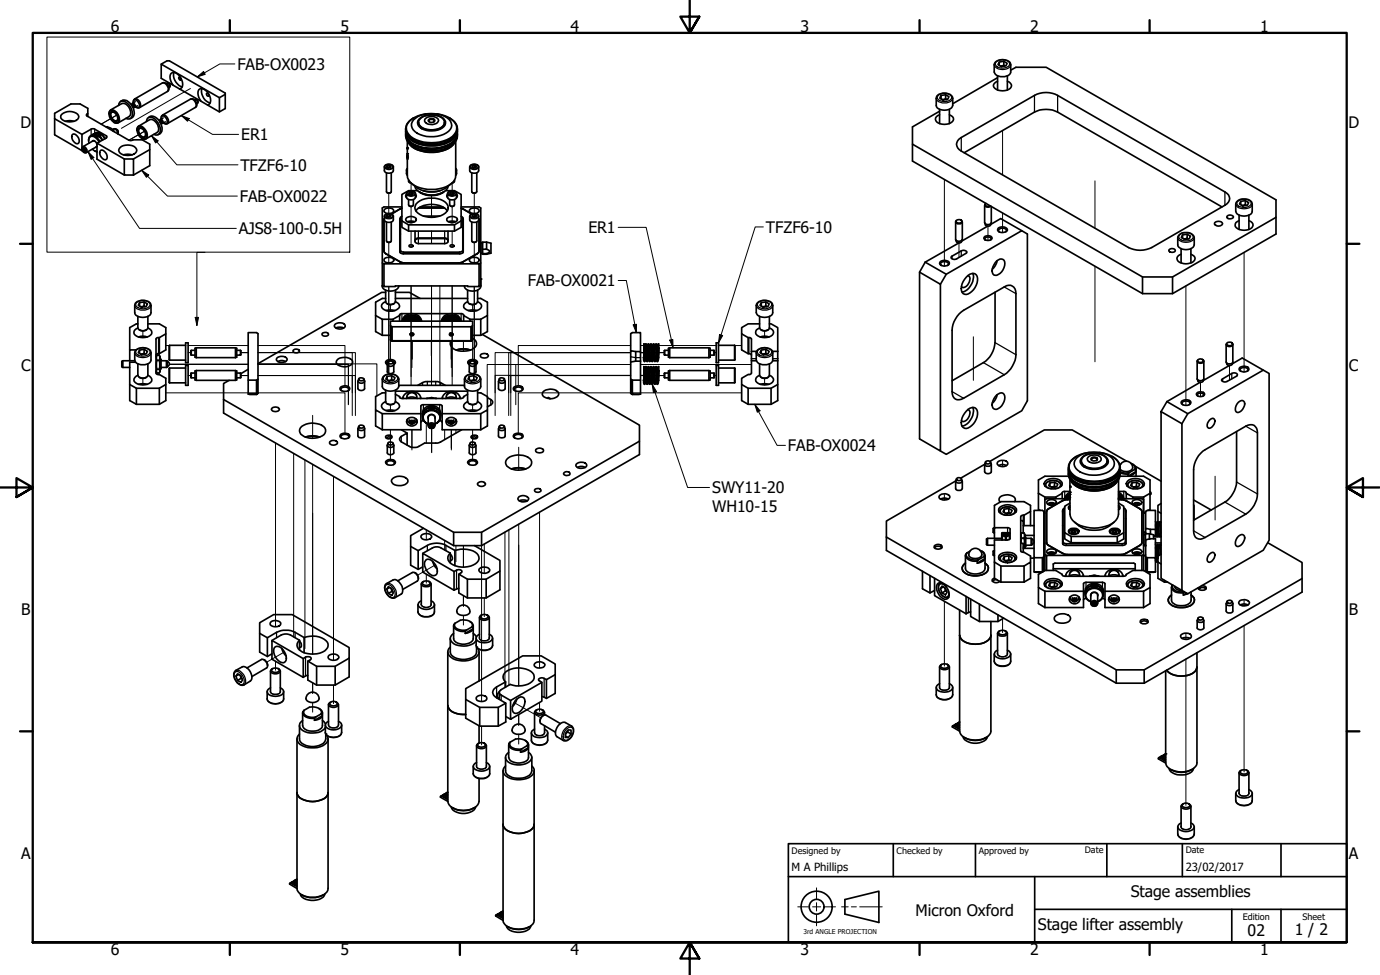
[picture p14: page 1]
Micron Oxford

Designed by M A Phillips | Checked by | Approved by Date | Date 23/02/2017

3rd ANGLE PROJECTION | | Stage assemblies

Stage lifter assembly | Edition 02 | Sheet 1 / 2

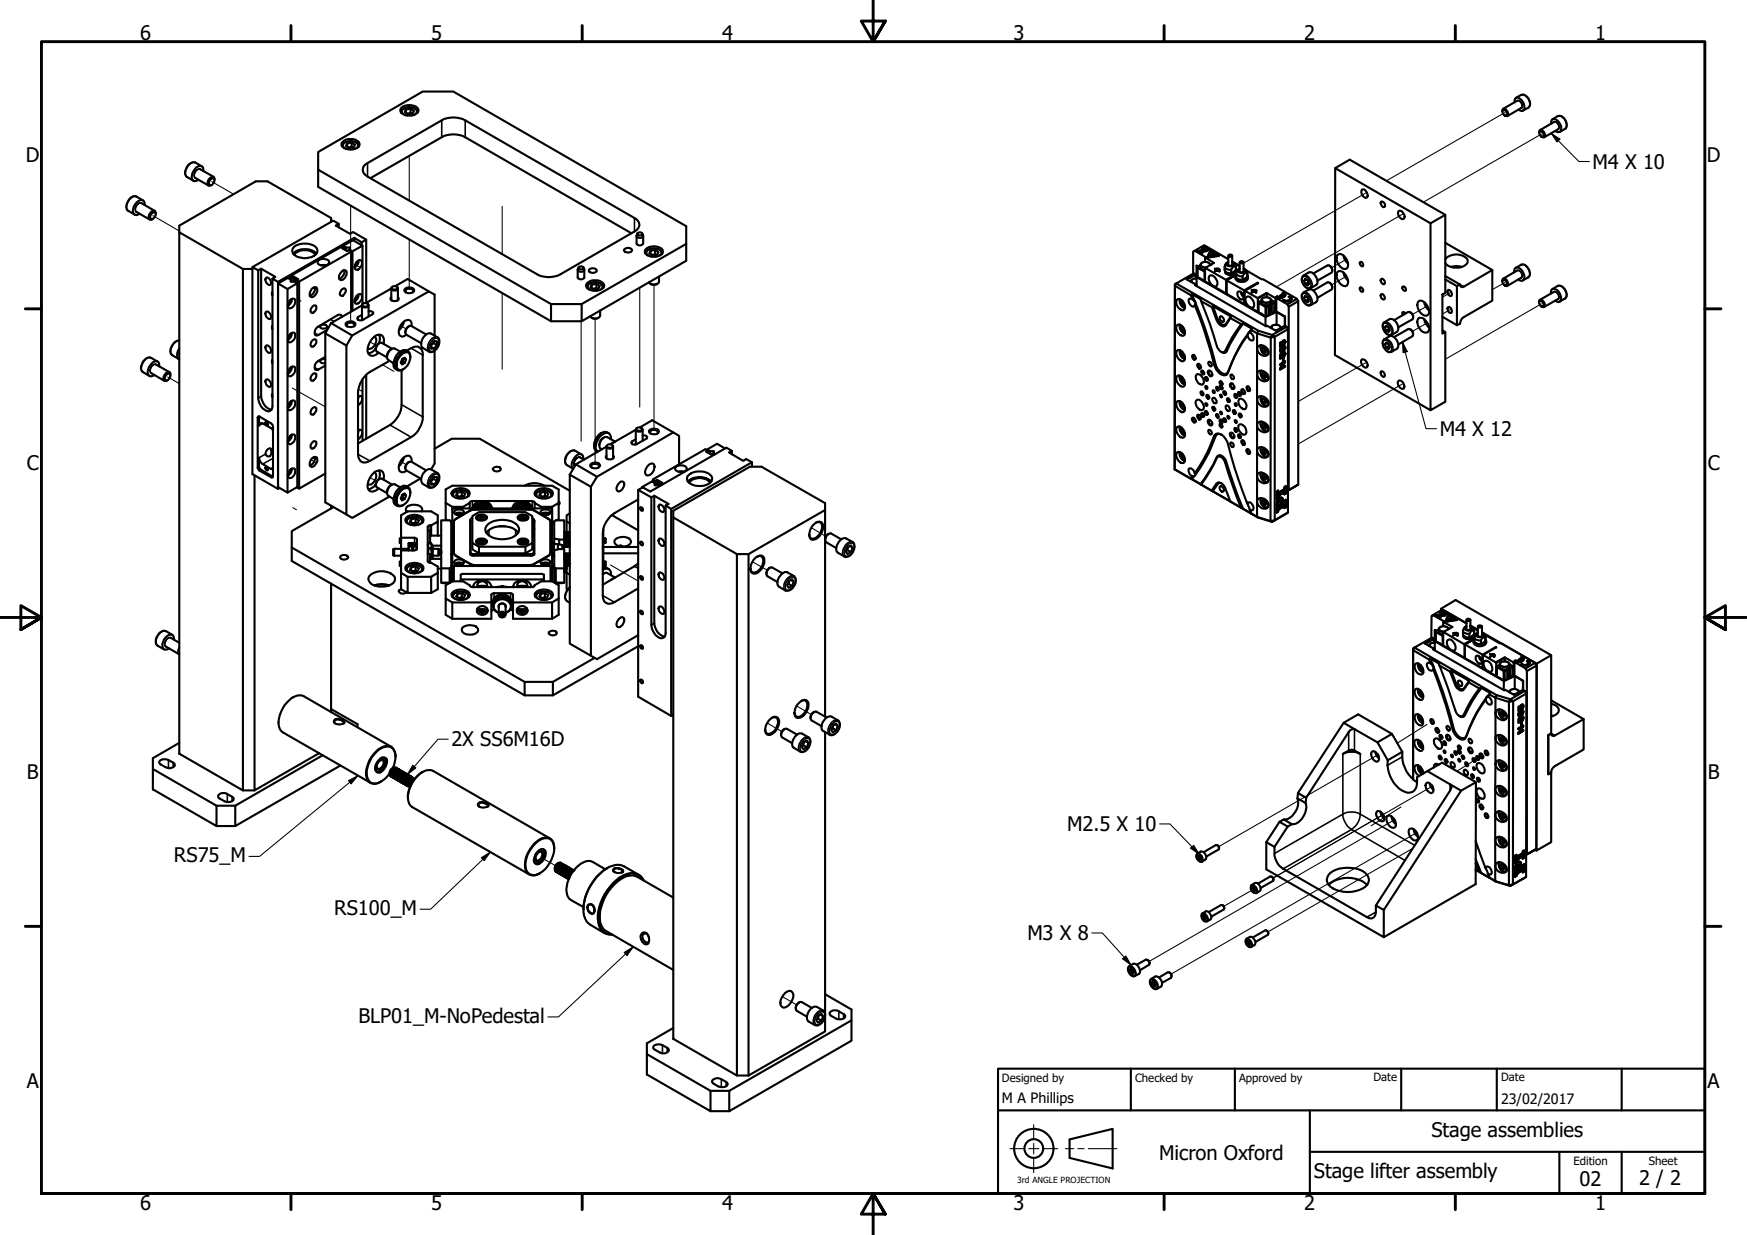
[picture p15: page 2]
Micron Oxford

Designed by M A Phillips | Checked by | Approved by Date | Date 23/02/2017

3rd ANGLE PROJECTION | | Stage assemblies

Stage lifter assembly | Edition 02 | Sheet 2 / 2

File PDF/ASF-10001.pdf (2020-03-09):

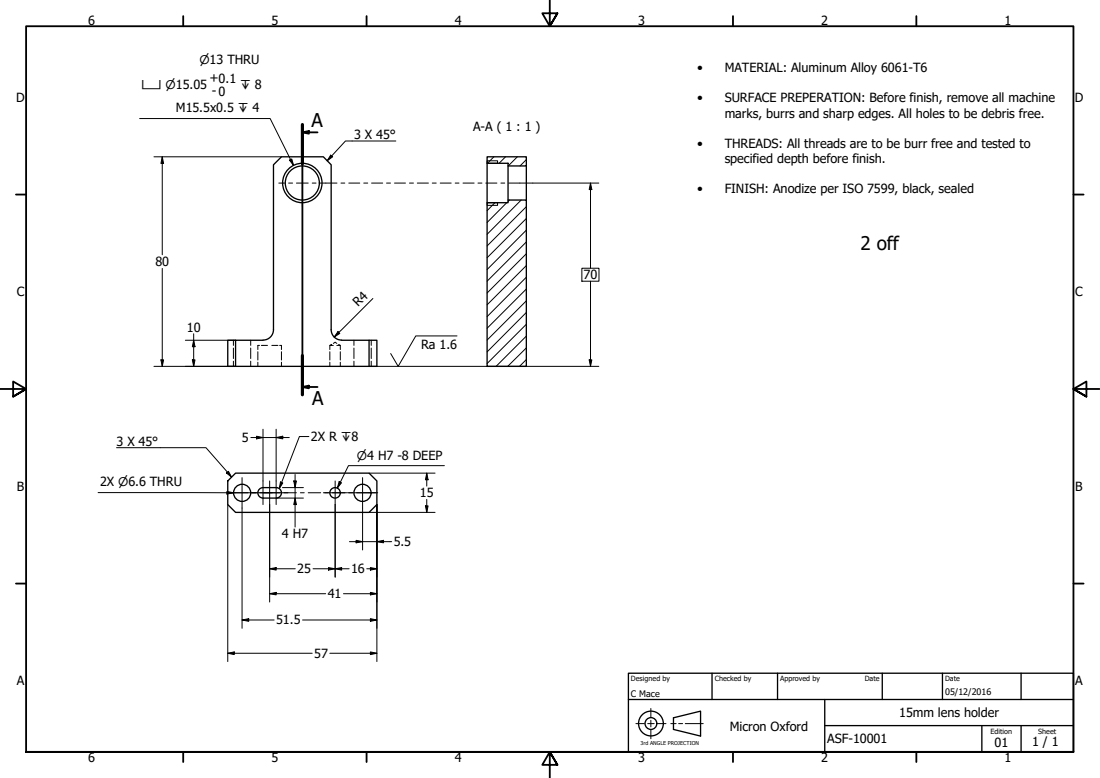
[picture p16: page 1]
Micron Oxford; 2 off

• MATERIAL: Aluminum Alloy 6061-T6

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

• THREADS: All threads are to be burr free and tested to
specified depth before finish.

• FINISH: Anodize per ISO 7599, black, sealed

Designed by C Mace | Checked by | Approved by Date | Date 05/12/2016

3rd ANGLE PROJECTION | | 15mm lens holder

ASF-10001 | Edition 01 | Sheet 1 / 1

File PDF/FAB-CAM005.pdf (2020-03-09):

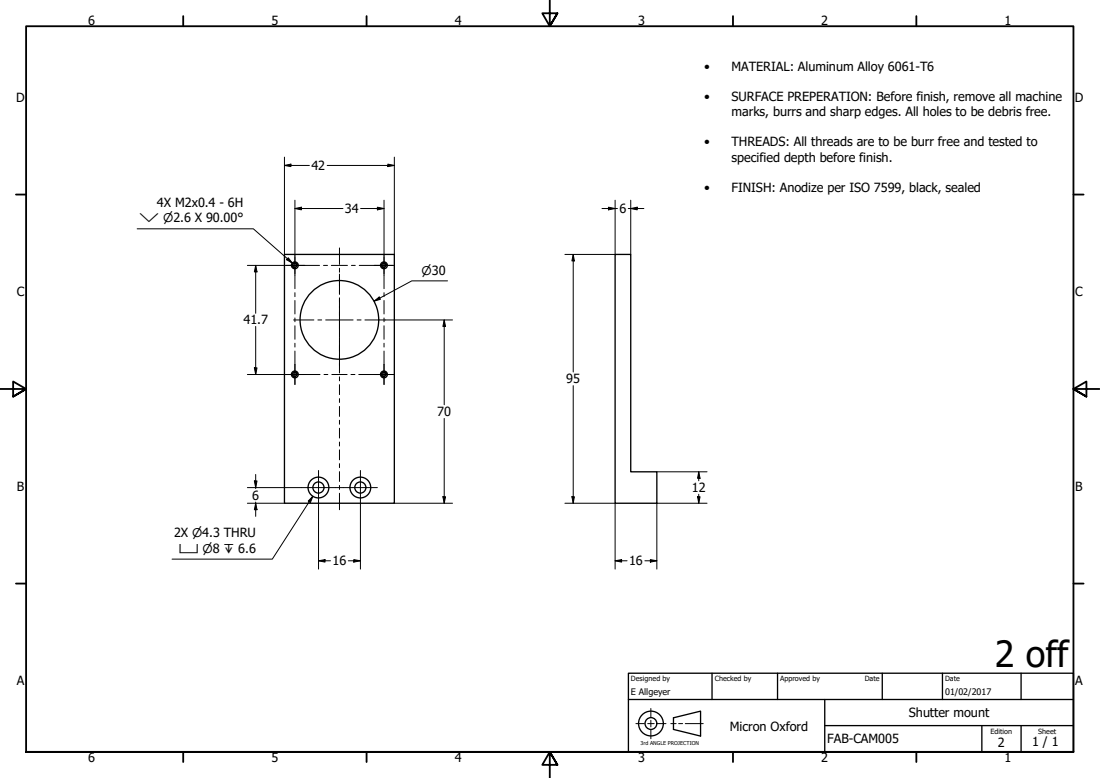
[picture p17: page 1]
Micron Oxford; 2 off

• MATERIAL: Aluminum Alloy 6061-T6

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

• THREADS: All threads are to be burr free and tested to
specified depth before finish.

• FINISH: Anodize per ISO 7599, black, sealed

Designed by E Allgeyer | Checked by | Approved by Date | Date 01/02/2017

3rd ANGLE PROJECTION | | Shutter mount

FAB-CAM005 | Edition 2 | Sheet 1 / 1

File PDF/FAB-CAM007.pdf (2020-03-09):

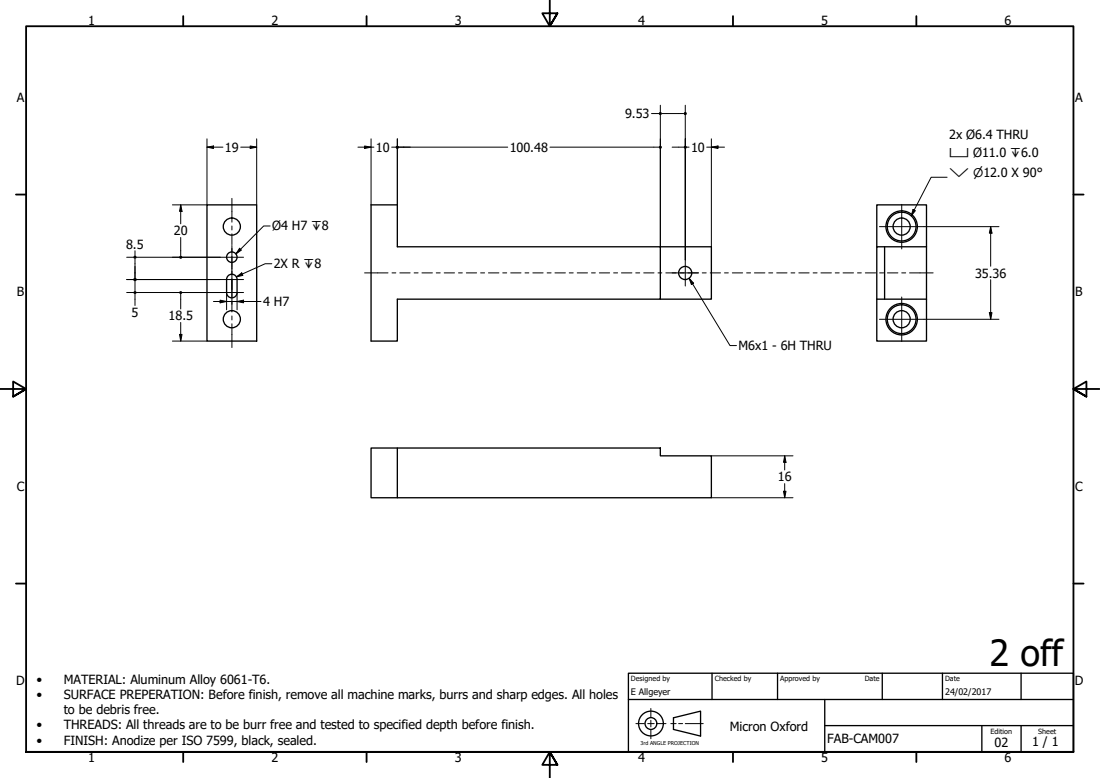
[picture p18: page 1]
Micron Oxford; 2x Ø6.4 THRU; M6x1 - 6H THRU; 2 off

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

Designed by E Allgeyer | Checked by | Approved by Date | Date 24/02/2017

FAB-CAM007 | Edition 02 | Sheet 1 / 1

3rd ANGLE PROJECTION

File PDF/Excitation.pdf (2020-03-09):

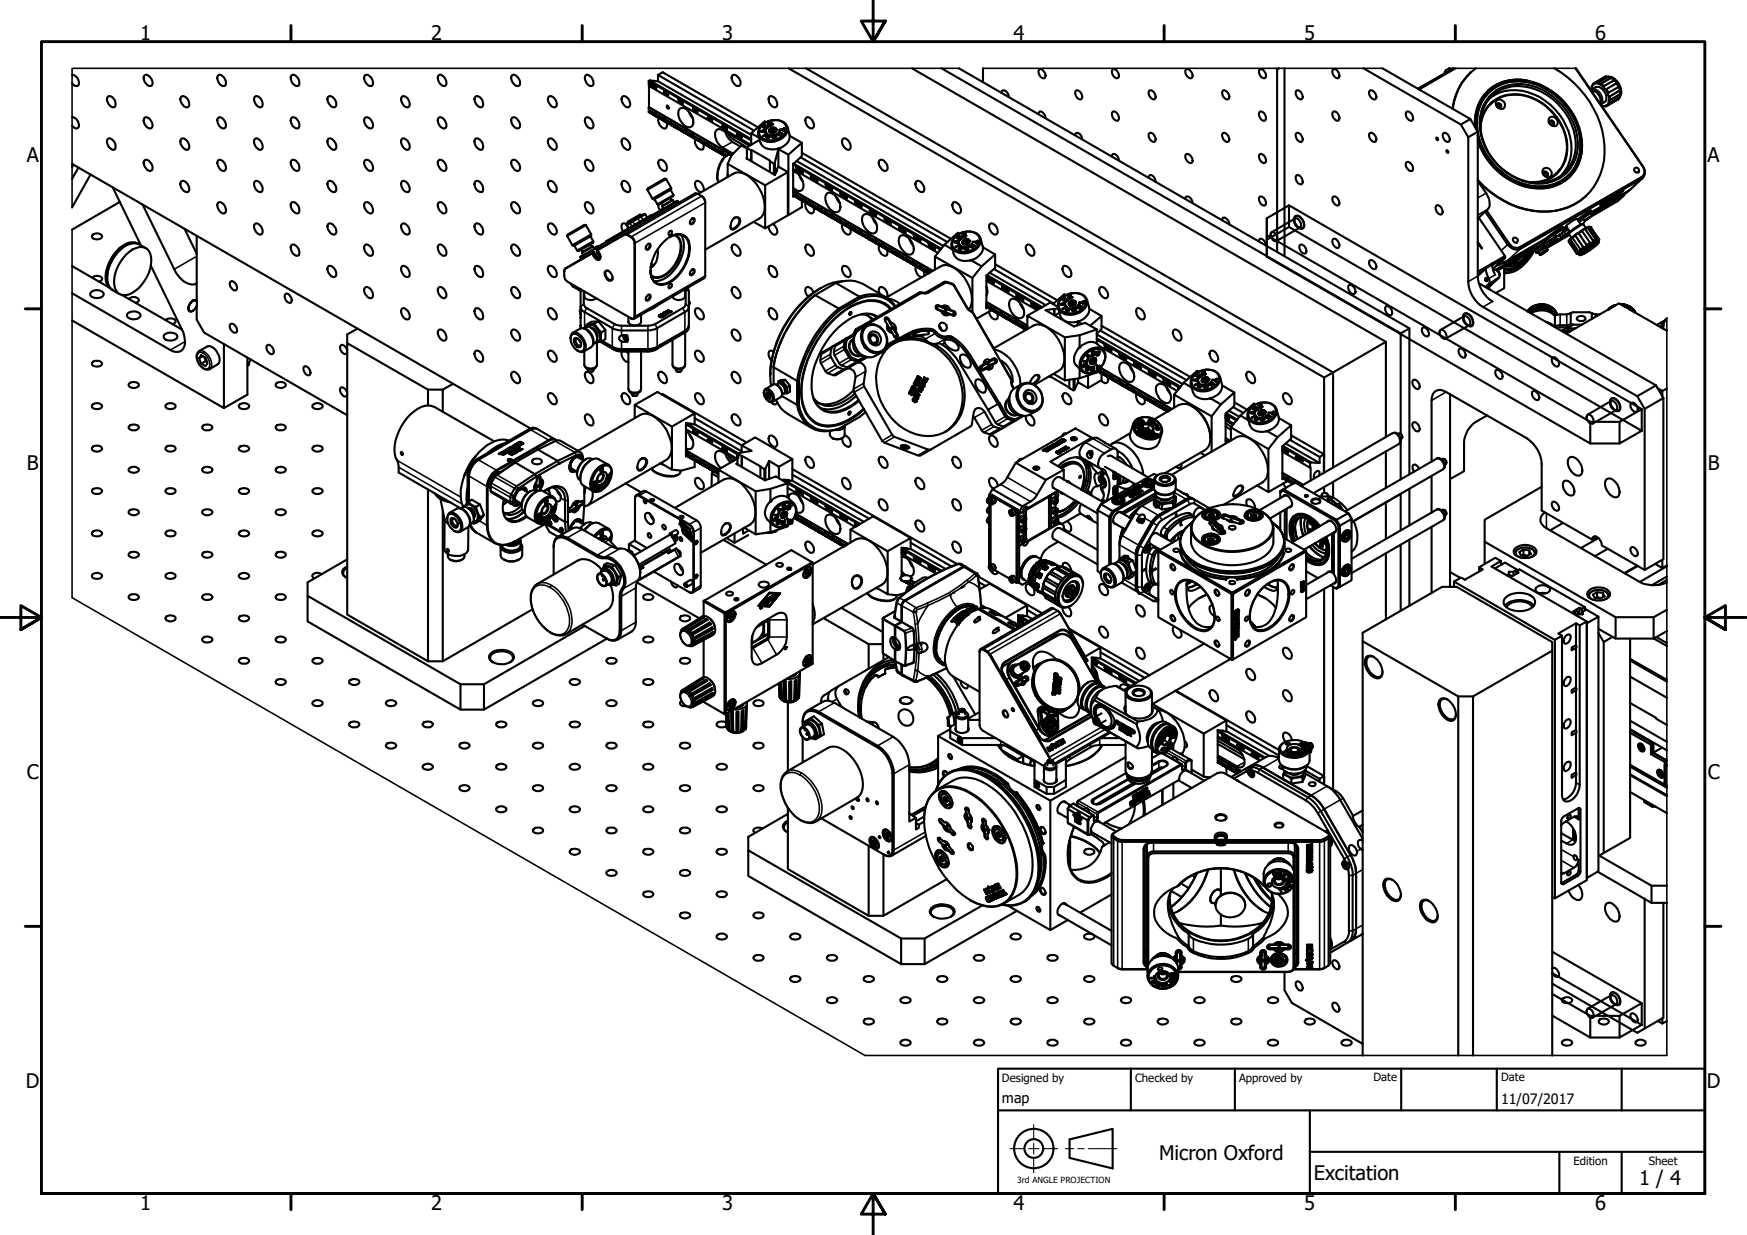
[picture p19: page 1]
Micron Oxford; Designed by; Checked by; Approved by; Date; 3rd ANGLE PROJECTION

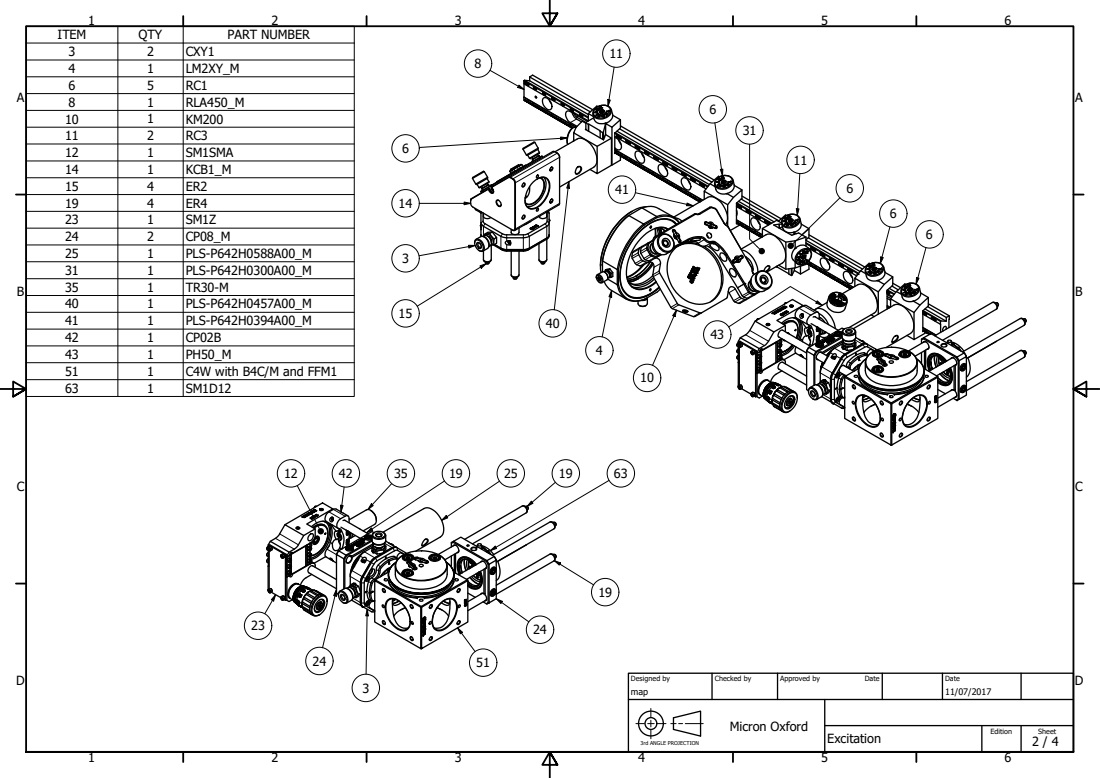
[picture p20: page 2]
ITEM; QTY; PART NUMBER; C4W with B4C/M and FFM1; Designed by; Checked by; Approved by; Date

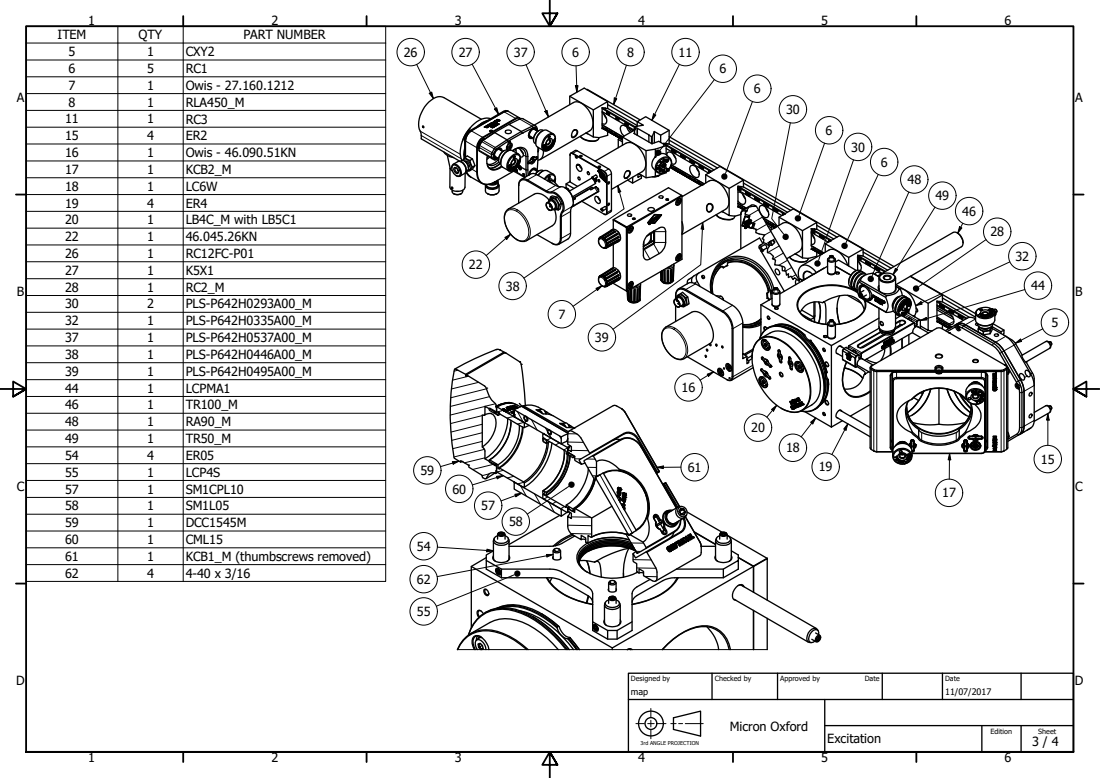
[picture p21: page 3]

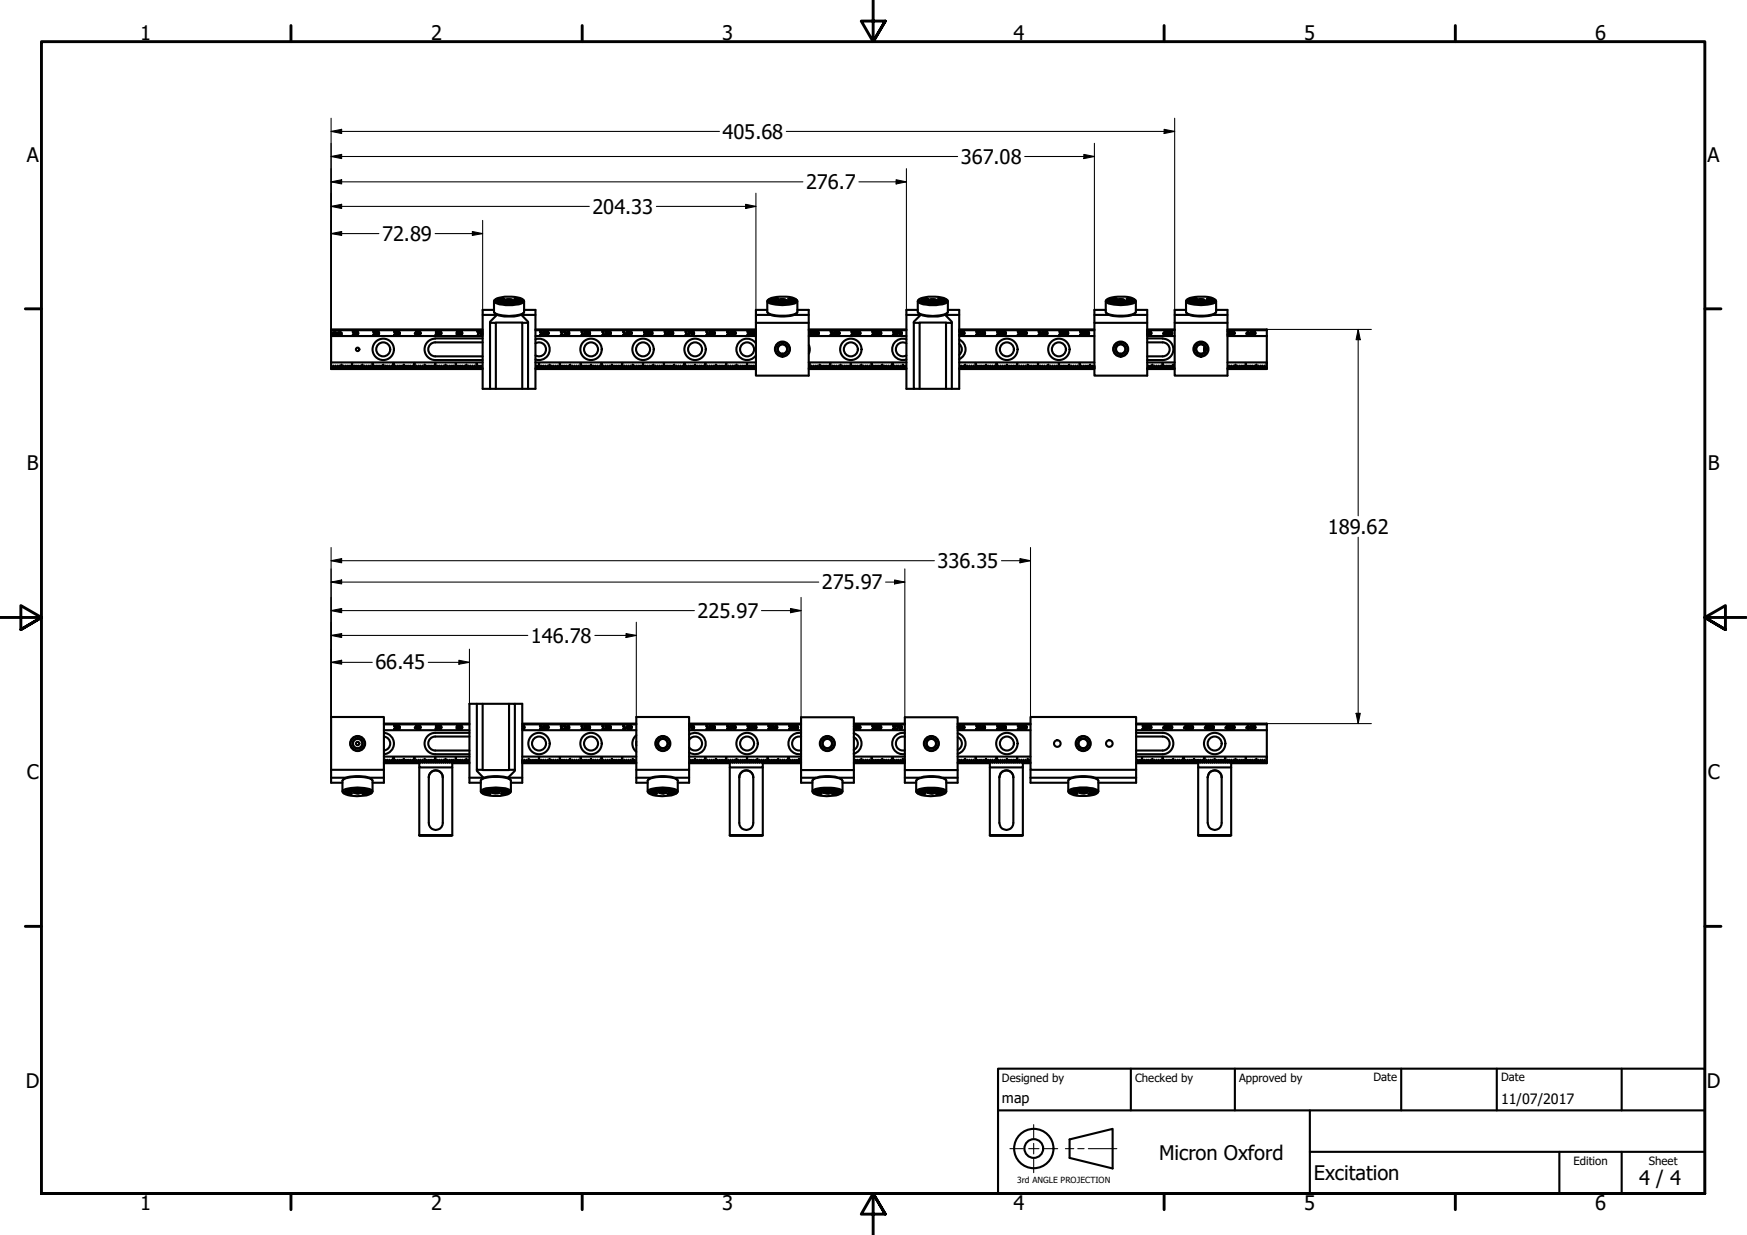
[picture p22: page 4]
Designed by; Checked by; Approved by; Date

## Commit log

2020-03-09 Brief description in Readme and added Inventor, Step and PDF files
    [0-PH-SMALL-1_M20_L40_4.ipt, 01-Bridge.iam, 02-CompensationAndCombination.iam, 03-ImageSeparation.iam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]
2020-03-17 Added parts list and updated README
    [PartsList.xlsx]
2020-03-17 updated parts list for excitation path changes
    [PartsList.xlsx]
2020-05-12 Added 3d print file of shutter mount
    [4pi-shutter-mount-V2 (2).stl]
2020-05-12 renamed shuuter stl file
    [4pi-shutter-mount-V2.stl]
2020-05-13 update to latest parts list 20200513
    [PartsList.xlsx]
2020-06-11 Removed parts that are not used in the Protocol manuscript.
    [PartsList.xlsx]
2020-06-12 Duplicates removed and same parts in different spaces combined.
    [PartsList.xlsx]
2020-06-12 Remove redundant sample clips
    [PartsList.xlsx]
2020-06-29 Remove price and some deleted parts
    [PartsList.xlsx]
2020-07-08 Update emission filter informatino and add some labels used in the Protocol figures
    [PartsList.xlsx]
2020-07-08 Update the dicrhoic filters to the latest
    [PartsList.xlsx]
2020-09-01 Added pupil plane camera directory and all needed files (these are Solidworks, not Inventor).
    [84-933 - Board Level Camera.SLDPRT, FAB-CH001 - Camera Holder.DXF, FAB-CH001 - Camera Holder.SLDDRW, FAB-CH001 - Camera Holder.SLDPRT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]
2021-01-07 added PartsList.csv as a csv file, maybe should be the only version?
    [PartsList.csv]
